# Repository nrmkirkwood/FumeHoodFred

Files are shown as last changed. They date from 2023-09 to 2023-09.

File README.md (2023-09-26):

# FRED assembly and installation instructions
FRED (Fumehood Reduction in Energy Device) is a simple, Raspberry Pi based retrofit device which mitigates emissions from fumehoods in research labs. Each FRED can reduce the amount of time a fume hood spends open by around 40% and a corresponding decrease in energy consumption (and carbon emissions!) of around 33%.

For a more detailed motivation, data proving that FRED works, and explanation of how the figures above are arrived at, see [my project post on FRED](https://nrmkirkwood.github.io/projects/fumehoodfred/).

This readme details how to assemble and install a 'basic' FRED with buzzers only (no Teams posting). For details on code and setup of an 'advanced' FRED with a RPi running Python with WiFi and Teams posts enabled, contact me.

# Assembling FRED

## Required equipment

You will need (AUD price as of September 2023 in brackets + links to suggested suppliers in Australia):

- Raspberry Pi Pico ([$6.30](https://core-electronics.com.au/raspberry-pi-pico.html))
- Power supply + cable ([supply $1.95](https://www.ebay.com.au/itm/284385278195), [cable $2.63](https://www.ebay.com.au/itm/384493783379))
- 'Reward' piezo buzzer 3V ([$3.15](https://core-electronics.com.au/piezo-buzzer-ps1240.html))
- 'Alarm' buzzer 3-5V ([$0.74](https://core-electronics.com.au/piezo-buzzer.html))
- Reed Door Switch Sensor ([$3.85](https://www.ebay.com.au/itm/154538574997))
- Code (Python) (from this repo: [fhf.py](https://github.com/nrmkirkwood/FumeHoodFred/blob/main/fhf.py))
- 3D printed case and lid (from this repo: [fhf-case](https://github.com/nrmkirkwood/FumeHoodFred/blob/main/fhf-case.stl) & [fhf-lid](https://github.com/nrmkirkwood/FumeHoodFred/blob/main/fhf-lid.stl))

You will also need:

- 3D printer (or, make your own case - or use without a case!)
- Soldering iron & solder (or, buy Pico with soldered headers, and use M-F jumper cables)
- Velcro strips (M+F) or double sided tape/strips
- A fume hood to put it in!

## Building FRED
Solder the alarm buzzer, reward buzzer, and Reed switch onto the Pico pins as indicated. The case provided assumes you solder the buzzers directly onto the Pico with no wires:

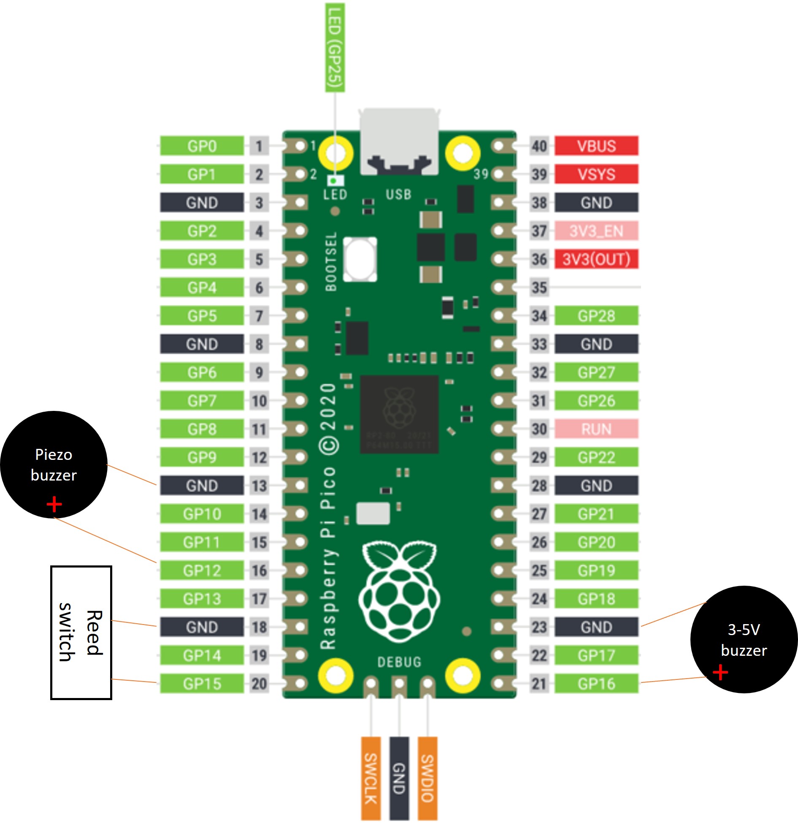
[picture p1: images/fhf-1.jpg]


The finished Pico should look like this:

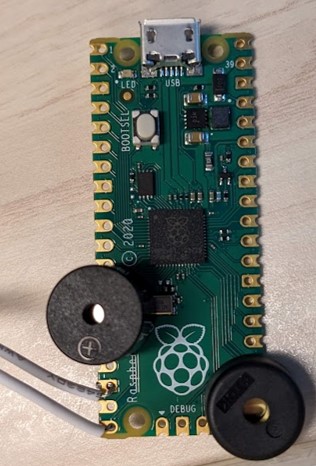
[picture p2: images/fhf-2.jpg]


3D print the [case](https://github.com/nrmkirkwood/FumeHoodFred/blob/main/fhf-case.stl) & [lid](https://github.com/nrmkirkwood/FumeHoodFred/blob/main/fhf-lid.stl). The Pico should fit snugly into the case. Use doubled sided tape to secure the wired Reed switch onto the top of case as pictured:

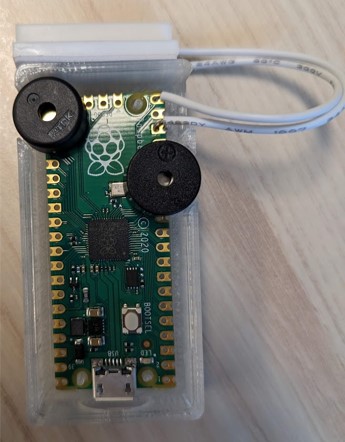
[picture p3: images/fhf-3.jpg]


Snap the lid on (it's a snap-fit so may require a little force). If desired draw a smiley face:

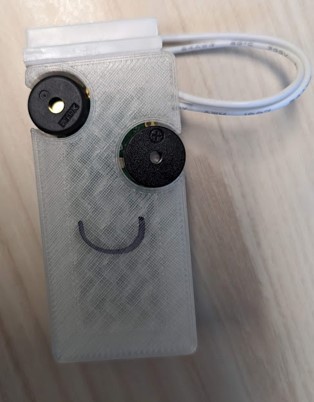
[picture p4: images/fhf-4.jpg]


At this stage, plug the RPi Pico into your computer and follow instructions to [install ThonnyIDE](https://projects.raspberrypi.org/en/projects/getting-started-with-the-pico/2), [setup MicroPython firmware](https://projects.raspberrypi.org/en/projects/getting-started-with-the-pico/3) and [use the shell to run code off the Pico](https://projects.raspberrypi.org/en/projects/getting-started-with-the-pico/4).

Load the [fhf.py code](https://github.com/nrmkirkwood/FumeHoodFred/blob/main/fhf.py) file in Thonny and [save to your Pico as main.py](https://projects.raspberrypi.org/en/projects/getting-started-with-the-pico/9). 

Now when you plug your Pico (now a FRED) into power, the onboard green LED should turn on. Move the Reed switches together and the LED should turn off and the reward buzzer should play a chromatic riff. If you leave the FRED on for 1 hour with the Reed switches apart, the alarm buzzer will sound. (You can test this for shorter time intervals by editing the main.py code and setting the alarm time to a few seconds).

If all works well the FRED is ready to install.

# Installing FRED into a fume hood

First attach Velcro or doubled-sided tape to the backside of the FRED case:

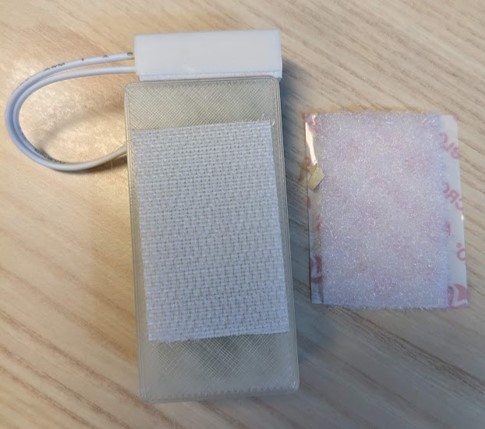
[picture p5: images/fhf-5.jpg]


To attached the FRED into the fume hood, pick a spot where the FRED can be close enough to the fume hood sash that there a < 1 cm gap between the Reed switches with the non-wired Reed switch on the sash *when the fume hood is fully closed*. Check this before sticking anything! Using Velcro stickers is handy as the FRED can be moved a bit after installation to optimise position. Some photos below show installation methods that work in our lab:

Inside the fumehood, with unwired Reed switch on the inside of the sash near bottom:

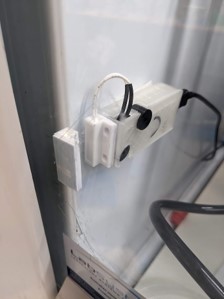
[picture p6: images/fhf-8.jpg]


Outside the fumehood (recommended if possible), with unwired Reed switch on the hand-grip of the sash:

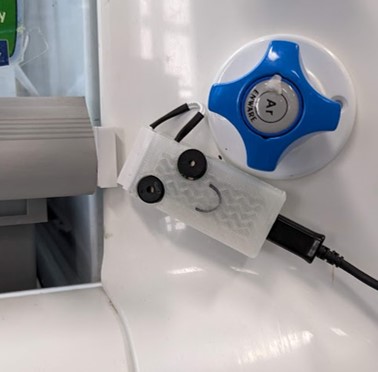
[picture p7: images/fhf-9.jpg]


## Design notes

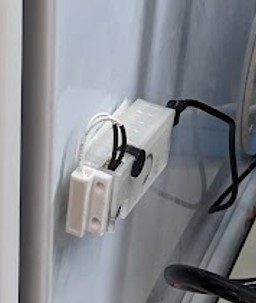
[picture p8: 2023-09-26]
images/fhf-7.jpg

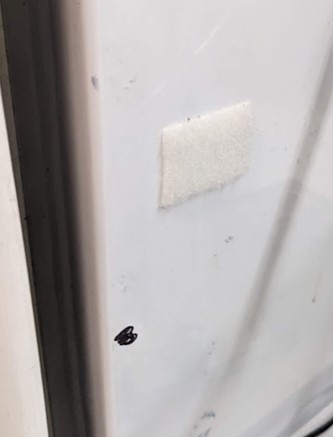
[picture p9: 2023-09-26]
images/fhf-6.jpg

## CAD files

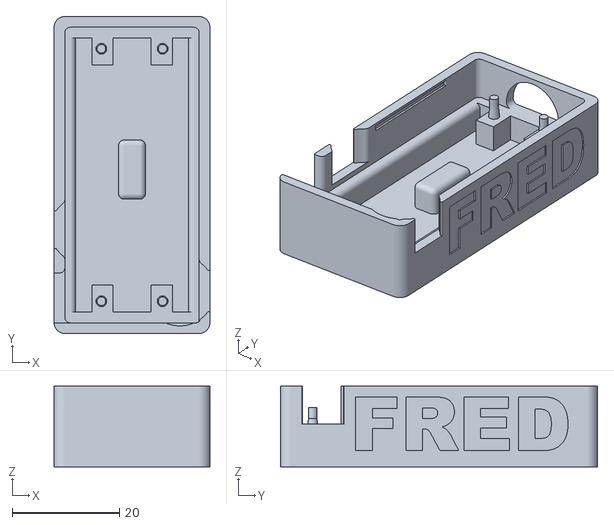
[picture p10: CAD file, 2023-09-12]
fhf-case.stl
29.0 x 59.0 x 15.0

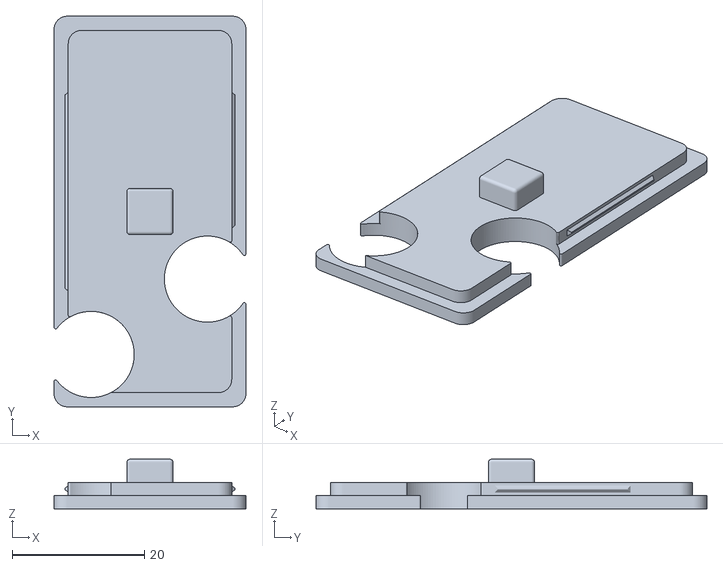
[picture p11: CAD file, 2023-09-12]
fhf-lid.stl
29.0 x 59.0 x 7.50

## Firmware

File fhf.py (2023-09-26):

from machine import Pin, PWM
import utime
import time

#fhf_basic_v1.2 - micropython code to run a FRED device using a RPi Pico 
#changes:
#v1.0 - created for use with Rpi Pico (no wifi)
#v1.1 - added melodies
#v1.2 - added data logs

### USER INPUTS REQUIRED IN THIS SECTION ###

# setup pins - these will need to change depending on where the buzzers and Reed switch are connected to the RPi Pico
led = Pin(25, Pin.OUT)
annoy_buzzer = Pin(12, Pin.OUT)     #PIN for the loudest buzzer you can get that works at ~3 V pinout of RPi (about 50% of cheap 5V buzzers seem to work OK)
reward_buzzer = PWM(Pin(16))        #PIN for a 3V piezo buzzer which allows different frequencies 
reed = Pin(15, Pin.IN, Pin.PULL_UP) #PIN for Reed switch sensor

#set silent = 1 for silent data logging; silent = 0 for normal operation with alarms etc.
silent = 0 

#set the time (in seconds) that fume hood is allowed to be left up before alarm (buzzer) activates
#recommend ~1 hr = 3600 seconds; too short and users will be annoyed if the alarm goes off during an experiment.
alarm_time = 3600

### FOLLOWING IS CODE TO BE LEFT ALONE UNLESS YOU WANT TO CHANGE STUFF ###

#initialise
#onboard LED off
led.low()

#buzzer off
annoy_buzzer.low()
reward_buzzer.duty_u16(0)

#wait before starting
utime.sleep(1) 

#set last closed time and status of fumehood as CLOSED to begin with
closed_last = time.ticks_ms()
fh_current = "CLOSED" 

#set some frequencies
tones = {
     'c': 262,
     'd': 294,
     'e': 330,
     'f': 349,
     'g': 392,
     'a': 440,
     'b': 494,
     'C': 523,
     ' ': 110,
     'H': 207,
     'X': 233,
     'F': 174,
     'E': 659
}

# set melody and timing. If you want you can change this to alter the reward melody
melody_reward = 'cdefgabC'
rhythm_reward = [8, 8, 8, 8, 8, 8, 8, 8]
tempo = 0.5

try:
    while True:
        #if the magnet is not detected (fh open) Reed sensor returns 1 (high):
        if reed.value() == 1: 
            if fh_current == "CLOSED":
                fh_current = "OPEN"           #change status to open
                #print ("Fume Hood OPEN")     #print status of fume hood (uncomment for debug) 
                start_time = time.time()      #record time when fumehood opened
            led.high()                         #turn on indicator LED
            now = time.time() - start_time     #now is in seconds
            if (now > alarm_time and silent == 0):
                annoy_buzzer.high()            #activate buzzer if the time exceeds alarm time set above                
        else:                                   #if the fume hood closes, reed.value will not be 1
            if (fh_current == "OPEN" and time.ticks_diff(time.ticks_ms(), closed_last) > 1000):   #set a 1000 ms buffer to avoid issues with sensors triggering false open events
                # print("Fumehood CLOSED. Time open (sec): " + str(now))   #print status of fume hood (uncomment for debug)
                #open log and input data
                file=open("fredlog.csv", "a")
                file.write("\n" + "Silent Mode:" + "\t" + str(silent) + "\t" + "Time open (sec):" + "\t" + str(now))
                file.close()
                #turn off LED and buzzer:
                led.low()
                annoy_buzzer.low()
                #record last close time in ms (see loop above - this is to stop sensor errors giving false open events):
                closed_last = time.ticks_ms()
                time.sleep(0.1)

                if silent == 0:
                    reward_buzzer.duty_u16(30000) #activate reward noise on closing
                    for tone, length in zip(melody_reward, rhythm_reward):
                        reward_buzzer.freq(tones[tone])
                        time.sleep(tempo/length)
                    reward_buzzer.duty_u16(0)
                fh_current = "CLOSED"  #set status as closed

#exit cleanly via ctrl+c
except KeyboardInterrupt:
    print ("Quit")
    led.low()
    annoy_buzzer.low()
    reward_buzzer.duty_u16(0)
    
finally:
    led.low()
    annoy_buzzer.low()
    reward_buzzer.duty_u16(0)
